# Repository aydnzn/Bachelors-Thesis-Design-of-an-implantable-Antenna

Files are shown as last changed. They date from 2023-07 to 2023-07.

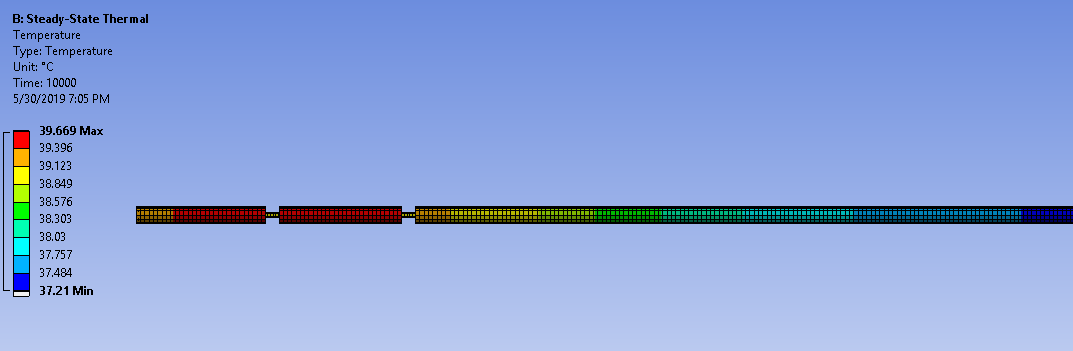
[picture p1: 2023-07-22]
Part I/figs/koichi_in_femur_son.PNG

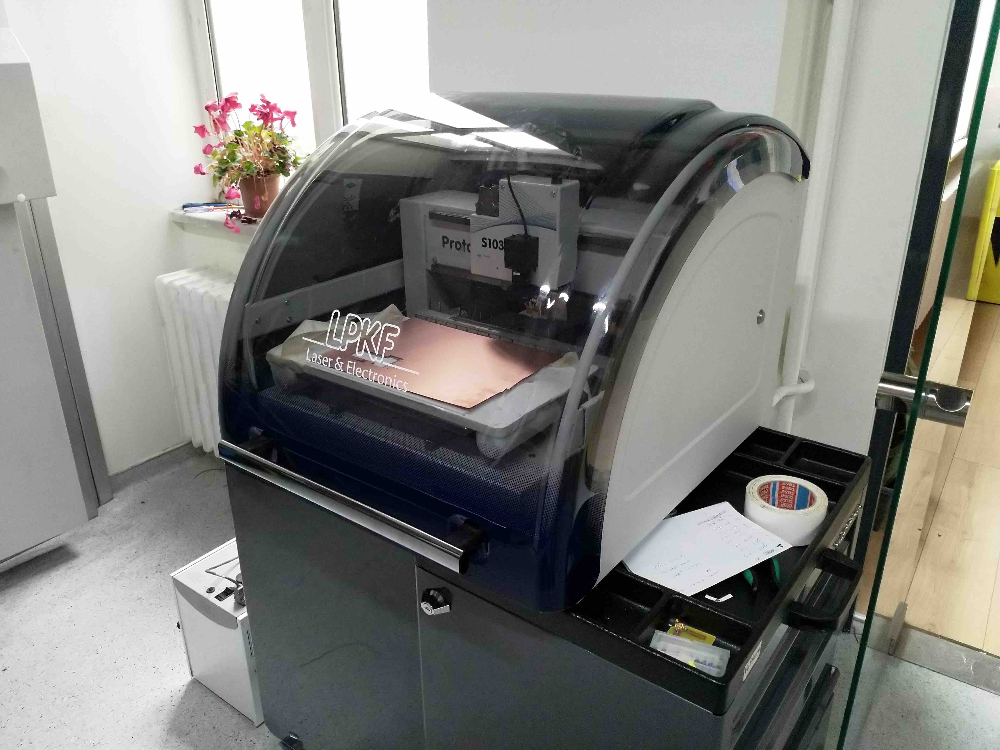
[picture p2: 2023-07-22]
Part II/photos/IMG_20191228_121618.jpeg

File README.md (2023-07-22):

# Bachelor's Thesis: Design of an Implantable Antenna for Microwave Hyperthermia

This Bachelor's thesis, divided into two distinct parts, explores the design of an implantable antenna for microwave hyperthermia. The work was conducted at the Antennas and Propagation Research Laboratory, [BOUNtenna](https://bountenna.boun.edu.tr), at Bogazici University under the guidance of [Assoc. Prof Sema Dumanli Oktar](https://academics.boun.edu.tr/sema.dumanli/).

To access individual parts of the thesis, use the following links: [Part I](./Part%20I/) and [Part II](./Part%20II/).

## Part I

### Project Aim

The primary goal of this project is to utilize technology to augment healthcare services. By designing implantable antennas, we aim to tackle the challenge of post-operative infections, especially those that occur post hip replacement surgeries. The rising trend of such surgeries and the subsequent need for revisions require innovative solutions to mitigate complications like infections. The proposed implants would use microwave hyperthermia to hinder biofilm formation, guided by real-time feedback from the antenna.

### Methodology and Analysis

#### Cavity-Backed Slot Antenna (CBSA)
CBSA was chosen due to its merits like low profile, light weight, and simple integration. Backed by a rectangular cavity for unidirectional radiation, CBSA was designed to operate at 2.4 GHz, a frequency allowed for body area networks or medical applications. The performance of CBSA was measured through return loss and radiation pattern, with the width and length of the stripline identified as crucial parameters post optimization.

#### Coaxial-Slot Antenna
Upon identifying the inadequacy of CBSA in providing adequate heating, a coaxial-slot antenna was modeled. This step validated the effectiveness of the thermal analysis setup, and due to its satisfactory SAR distribution and thermal analysis, the coaxial-slot antenna was chosen as a feasible solution.

#### C-Type Slotted Antenna
A C-type slotted antenna was designed to yield larger SAR values, simulating its performance within a hip implant. Though the heating was improved compared to CBSA, it didn't meet the set criterion for microwave hyperthermia (heating up to 40 °C).

### Conclusion and Future Work

Part I of this project encapsulates the development and simulation of implantable antennas with the aim to combat microwave hyperthermia. Despite facing challenges like defining an exact medium for simulation and limited documentation on Ansys Workbench for biomedical applications, significant knowledge was gained in utilizing HFSS and Workbench software applications.

Future work will focus on designing an antenna with superior heating performance. A wider range of antenna types will be explored and tested with the objective of finalizing a specific design for prototyping. Simulations will be concluded, and the prototyping phase will commence in the subsequent academic semester.

## Part II

This phase began with validating the thermal analysis from Part I, followed by designing a prototype antenna designed for heating at different frequencies. However, limitations led to a shift towards a miniaturized antenna design.

### Methodology

The methodology followed was sequential, starting with prototype antenna design, followed by miniaturized antenna design and measurement setup, phantom development, and concluding with thermal measurements.

A key part of this methodology was identifying the antenna's optimal operating frequency that leads to ideal SAR distribution, a process referred to as heating optimization.

### Prototype Antenna Design
The prototype design was a circular slot antenna, designed to operate at varying frequencies by adjusting the size of the slot. However, limitations arose while testing different frequencies with this setup.

### Miniaturized Antenna Design

Due to limitations faced during the prototype design phase, a transition was made to a more complex miniaturized antenna design, which offered the needed flexibility for testing across different frequencies.

### Measurement Setup

Considerations shifted towards post-production antenna measurements. The material was changed from human bone cortical to human fat for easier phantom production. The antenna was redesigned in the simulation program to fit in the measurement cup, and a feeding structure was added.

### Phantom Development

Phantom development was based on the methodology in this [article](https://ieeexplore.ieee.org/document/7152875), creating an artificial breast phantom replicating the dielectric and thermal properties of human fat. After adjusting the ratios of gelatin, water, and oil, the phantom's dielectric properties proved satisfactory.

### Antenna Production

Antenna production was done using an LPKF device, an in-house printed circuit board prototyping tool. The designed antenna's gerber files were loaded into the LPKF device, after which the feeding structure was soldered onto the antenna.

### Thermal Measurement

Heating at an input power of 6dbm was unobservable due to insufficient measuring equipment. As a result, input power was increased, using a signal generator from another lab. The results obtained were both intriguing and satisfactory.

### Conclusion

Despite several challenges, the project successfully led to the development and simulation of an implantable antenna operating at a frequency of 2.45 GHz. This project provided great learning opportunities and highlighted potential areas for further research and improvements.

### Cost Analysis

The project required a workstation for simulations, a vector network analyzer (VNA), a rotary stage, and absorbers for measurement setup.

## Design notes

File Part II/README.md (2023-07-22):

# Bachelor's Thesis: Design of an Implantable Antenna for Microwave Hyperthermia (Part II)

Welcome to the GitHub repository for the second part of the Bachelor's Thesis. This project focuses on the design of an implantable antenna for microwave hyperthermia. 

This repository contains the second phase of the project, discussing the methodology and analysis undertaken. The initial steps involved verifying the thermal analysis conducted in the previous phase, followed by the design of a prototype antenna for variable frequency heating. Due to encountered limitations, a transition was made to a miniaturized antenna design.

## Methodology

The adopted methodology was a sequential process, starting with the prototype antenna design, followed by the miniaturized antenna design and measurement setup. The subsequent steps involved phantom development and culminated in thermal measurements.

The critical aspect of this methodology was the identification of the optimal operating frequency for the antenna, resulting in ideal SAR distribution - a process also known as heating optimization.

## Prototype Antenna Design

A circular slot antenna served as the prototype design. The design aimed to function at varying frequencies, enabled by changing the size of the slot - the diameter of the inner circle and the width of the slot. Limitations were encountered when testing various frequencies in this setup.

## Miniaturized Antenna Design

The limitations from the prototype antenna prompted a transition to a more intricate miniaturized antenna design. Despite its complexity, this antenna offered the flexibility needed for testing across different frequencies.

## Measurement Setup

The measurement setup phase involved consideration of measurements post-antenna production. The material switched from human bone cortical to human fat for easier phantom production. The antenna was then redesigned in the simulation program to fit into the measurement cup, and a feeding structure was added.

## Phantom Development

Phantom development followed an [article](https://ieeexplore.ieee.org/document/7152875) outlining the creation of an artificial breast phantom replicating the dielectric and thermal properties of human fat. After adjusting the ratios of gelatin, water, and oil, the dielectric properties of the produced phantom proved satisfactory.

## Antenna Production

An LPKF device, an in-house printed circuit board prototyping tool, was used for antenna production. The designed antenna's gerber files were introduced to the LPKF device, after which the feeding structure was soldered onto the antenna.

## Thermal Measurement

At an input power of 6dbm, the heating provided was unobservable due to insufficient measuring equipment. This issue prompted an increase in input power, utilizing a signal generator from another lab. The resultant data were both intriguing and satisfactory.

## Conclusion

Despite a few challenges, a successful development and simulation of an implantable antenna operating at a frequency of 2.45 GHz was accomplished. This project offered invaluable learning opportunities and highlighted areas for potential improvements and further research.

## Cost Analysis

This project necessitated a workstation for simulation implementation and a vector network analyzer (VNA), a rotary stage, and absorbers for the creation of the measurement setup. 

## Repository Structure

This repository holds significant resources and documents pertinent to the project:

- `./scripts` : Contains MATLAB scripts for testing the dielectric properties of the phantom.
- `./designs/` : Holds ANSYS Electronics Desktop (AEDT) files used for various antenna designs throughout the project.
- `./VNA/` : Presents the results from the Vector Network Analyzer.
- `./manufacturing/` : Houses design files used in the fabrication of antennas, boards, etc. 
- `./thermal_photo/` : Features thermal camera screenshots to examine the heat generated by the fabricated antenna.
- `./photos/` : Provides an inside look into the manufacturing and measuring processes through photos.
- `after_graduation.zip` : Contains documents created post-graduation, furthering the work on this project for approximately 3-4 months until the onset of the pandemic.
- `Project_proposal.pdf`: Initial proposal for the project.
- `Midterm_report.pdf`: Midterm report, submitted on 20.11.2019.
- `Presentation.pdf`: Final presentation for this part of the thesis.
- `Bachelor's_Thesis.pdf`: Final bachelor's thesis, submitted on 4th January 2020.
- `./figs/`: Features a collection of screenshots taken during the simulation phase of the research.

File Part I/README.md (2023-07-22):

# Bachelor's Thesis: Design of an Implantable Antenna for Microwave Hyperthermia (Part I)

Welcome to the GitHub repository for the first part of my Bachelor's Thesis on the design of an implantable antenna for microwave hyperthermia. 

## Introduction

This project aims at advancing healthcare by designing an implantable antenna that can combat infections, particularly those that follow hip replacement surgeries. Given the increased trend in hip replacement surgeries and the concomitant need for revisions, a significant focus has been placed on developing solutions to alleviate complications such as infection. These implants are envisioned to use microwave hyperthermia to prevent biofilm formation, facilitated by real-time feedback from the antenna.

## Methodology and Analysis

### Cavity-Backed Slot Antenna (CBSA)
A CBSA, backed with a rectangular cavity for unidirectional radiation, was chosen for its benefits including low profile, light weight, and ease of integration. The CBSA was designed to operate at 2.4 GHz, an allowed band for body area networks or medical applications. The CBSA's performance was assessed in terms of return loss and radiation pattern. After optimization, the most critical parameters identified for matching were the width and the length of the stripline.

### Coaxial-Slot Antenna
After establishing that CBSA cannot provide adequate heating, a coaxial-slot antenna was modeled, which confirmed the success of my thermal analysis setup. The coaxial-slot antenna's SAR distribution and thermal analysis were found satisfactory, hence, it was deemed a viable solution.

### C-Type Slotted Antenna
A C-type slotted antenna was designed to achieve larger SAR values, simulating its performance within a hip implant. Although the heating was improved compared to the CBSA, it did not meet the evaluation criterion for microwave hyperthermia (heating up to 40 °C).

## Conclusion

The project described the development and simulation of implantable antennas aimed at counteracting microwave hyperthermia. Despite challenges such as defining an exact medium for simulation and acquiring limited documentation on using Ansys Workbench for biomedical purposes, substantial learning outcomes were achieved in using the HFSS and Workbench software applications.

## Future Work

The next stages of the project will focus on designing an antenna that demonstrates better heating performance. More antenna types will be reviewed and tested with a goal to finalize a specific antenna for prototyping. Simulations will be completed and the prototyping phase will commence in the next academic semester.

## Repository Structure

This repository contains several important documents and resources related to my project:

- `Project_proposal.pdf`: This document contains the initial proposal for my project.
- `Midterm_report.pdf`: This is my midterm report, which was submitted on 20th March 2019.
- `Presentation.pdf`: Here, you'll find my final presentation for this part of my thesis.
- `Final_report.pdf`: This document is the final report for this part of my thesis, which was submitted on 1st June 2019.
- `./figs/`: This directory contains several screenshots taken during the simulations conducted as part of my research.

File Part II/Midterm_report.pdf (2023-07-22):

EE492

# Senior Design Project Midterm Report

# Design of an implantable antenna for microwave hyperthermia

## Submitted by: Aydın Uzun

## Principal Investigator: Sema Dumanlı Oktar

20.11.2019

### 1. Introduction

The recent technological advancements are revolutionizing the way healthcare is being delivered and they are also a key factor driving the advances of surgical treatment. Joint replacement surgery (hip and knee replacement) is considered the most effective intervention for severe osteoarthritis and hip fractures, reducing pain and disability and restoring some patients to near normal function. [1] As a consequence, hip replacement surgery shows increasing trends in most OECD countries. On average, the rate of hip replacement increased by 30% between 2000 and 2015.[1] Revision burden can be seen as a rough measure of the success of hip replacement surgeries. In the USA the revision burden was 10.2% for hips between 2012 and 2015 [2], but revision surgery of the hip is expensive owing to the increased cost of pre-operative investigations, surgical implants and instrumentation. [3]

The six most common indications for revision after primary hip replacement (listed in order of frequency) are aseptic loosening, pain, adverse soft tissue reaction to particulate debris, dislocation, infection and peri-prosthetic fracture.[4] Especially performing the revision surgery for infection is riskier considering the instrumentation. Staphylococcus aureus and Staphylococcus epidermidis are the leading etiologic agents of orthopedic implant infection.[5] Traditional antibiotic therapy will never be successful against these pathogens after the biofilm is formed. [6] This property of bacteria is called antimicrobial resistance (AMR) and it is a major concern worldwide. The other modes of treatment will be needed to prevent biofilm formation in the first place.

A hip implant can be equipped with sensors and microelectronics forming a wireless communication link between the implant and an on-body sensor to collect continuous data or provide real-time feedback.[7] In this project it is aimed to design an antenna taking action against infection before and during the biofilm formation through microwave hyperthermia with the help of the feedback from the antenna which monitors its environment.

### 2. Objectives

The objective of this project is to take action against infection through microwave hyperthermia. In this context, the electrical characteristics of the tissue surrounding the implant will be determined immediately after the operation. (when the infection is present) In addition to that, numerical and physical modelling of the propagation environment will be performed. After all of the optimizations are completed, the optimum working frequency for the microwave hyperthermia will be determined and the antenna design will be completed.

The second objective of this project is to develop the phantom and to build the measurement setup on which the measurements will be performed next semester.

### 3. Approach and Methodology

a. Optimizations for microwave hyperthermia

Because the human body absorbs electromagnetic waves it is often difficult to connect an implanted device to the outside world. The effect of hyperthermia depends on the depth of the implant, surrounding tissues and near field losses. It should be noted that the surrounding tissue properties and depth of the implant vary from patient to patient, but only in one patient as the patient ages. Therefore, an antenna which can adapt to the changing environment and target energy to the required region should be designed for microwave hyperthermia. The antenna parameters will be optimized considering both the thermal and electromagnetic distribution.
b. Phantom development and building of measurement setup

1- Digital 3D design of the phantom model

A 3D model will be developed to mimic the environment in which the hip implant will be located in real life. The model should include the hip implant, a portion of the femur, pelvis, body fluid, hip muscle, fat and skin.
2- The integration of 3D phantom model with liquid/gel phantoms

The printed 3D model should be filled up with liquid/gel in accordance with the approximate dielectric constant and conductivity values of the corresponding parts described above.
3- Development of measurement setup

A test kit will be developed for measuring the input response and the transmission response of the designed antenna. The test kit will consist of a mini vector network analyzer (VNA), a rotary stage and absorber material. The test kit will be used in system level tests too.

### 4. Work Completed

In the first part of the project (EE 491), great progress had been made. You can review my previous reports to see what I did. At the beginning of the semester a meeting was held with my supervisor and we talked about what we are going to do this semester.

It was important to test that we did the thermal analysis correctly. The coaxial-slot antenna of Koichi Ito is designed and tested accordingly. The further explanation can be found on the final report of first part of the project.

The first task of this semester was to design a prototype antenna to test heating at different frequencies. One can see the prototype antenna and measurement setup on Figure
1. It is a circular slot antenna. To operate this antenna at the different frequencies (0.5 GHz to 2.5 GHz) one should definitely change the size of the slot in other words change the diameter of the inner circle and the width of the slot. One can also the change of the slots of antennas operating at 2 GHz and 2.5GHz on Figure 2 and Table 1.

This first task was very critical, because doing this we can find the optimum operating frequency value of the antenna which results in perfect SAR distribution. This process is also called heating optimization. It is clear that the heating occurs because of near field losses and it is frequency dependent. We have the possibility to test different frequencies unlike the Koichi’s circular slot antenna, because for our purposes only the specific small neighborhood of the antenna is important, not the depth or area of the heated region.

To determine the antenna’s working frequency is also important because I should also get a transmitter which works at this frequency value. So, it is an initial step for prototyping.

This was a simple setup as one can also see on Figure 1, but things did not go the way we wanted. We concluded that testing different frequencies is difficult in this setup. The limitation was that I could not change the antenna size as much as I wanted. To overcome this obstacle, it was decided to use a miniaturized antenna. The setup can be seen on Figure3. This design is initially made by my supervisor Prof. Sema Dumanlı Oktar. It is a complex design and was a little bit hard to understand. But after spending some time on the model I got it.

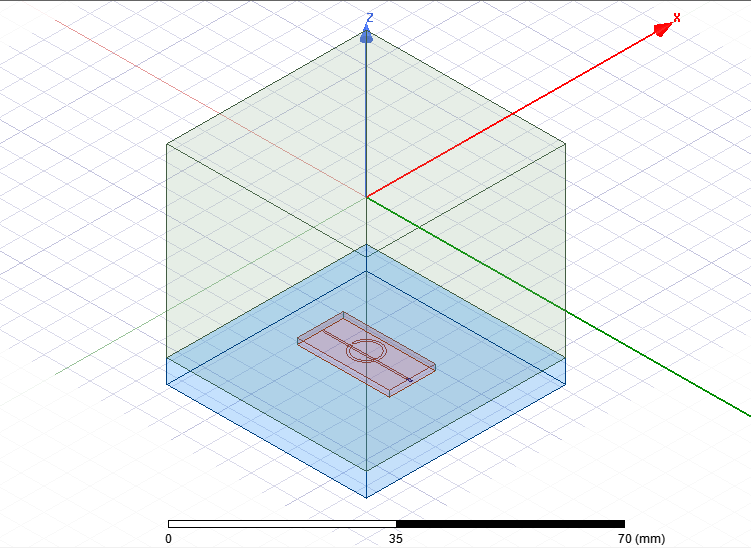
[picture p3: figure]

Figure 1: Measurement setup

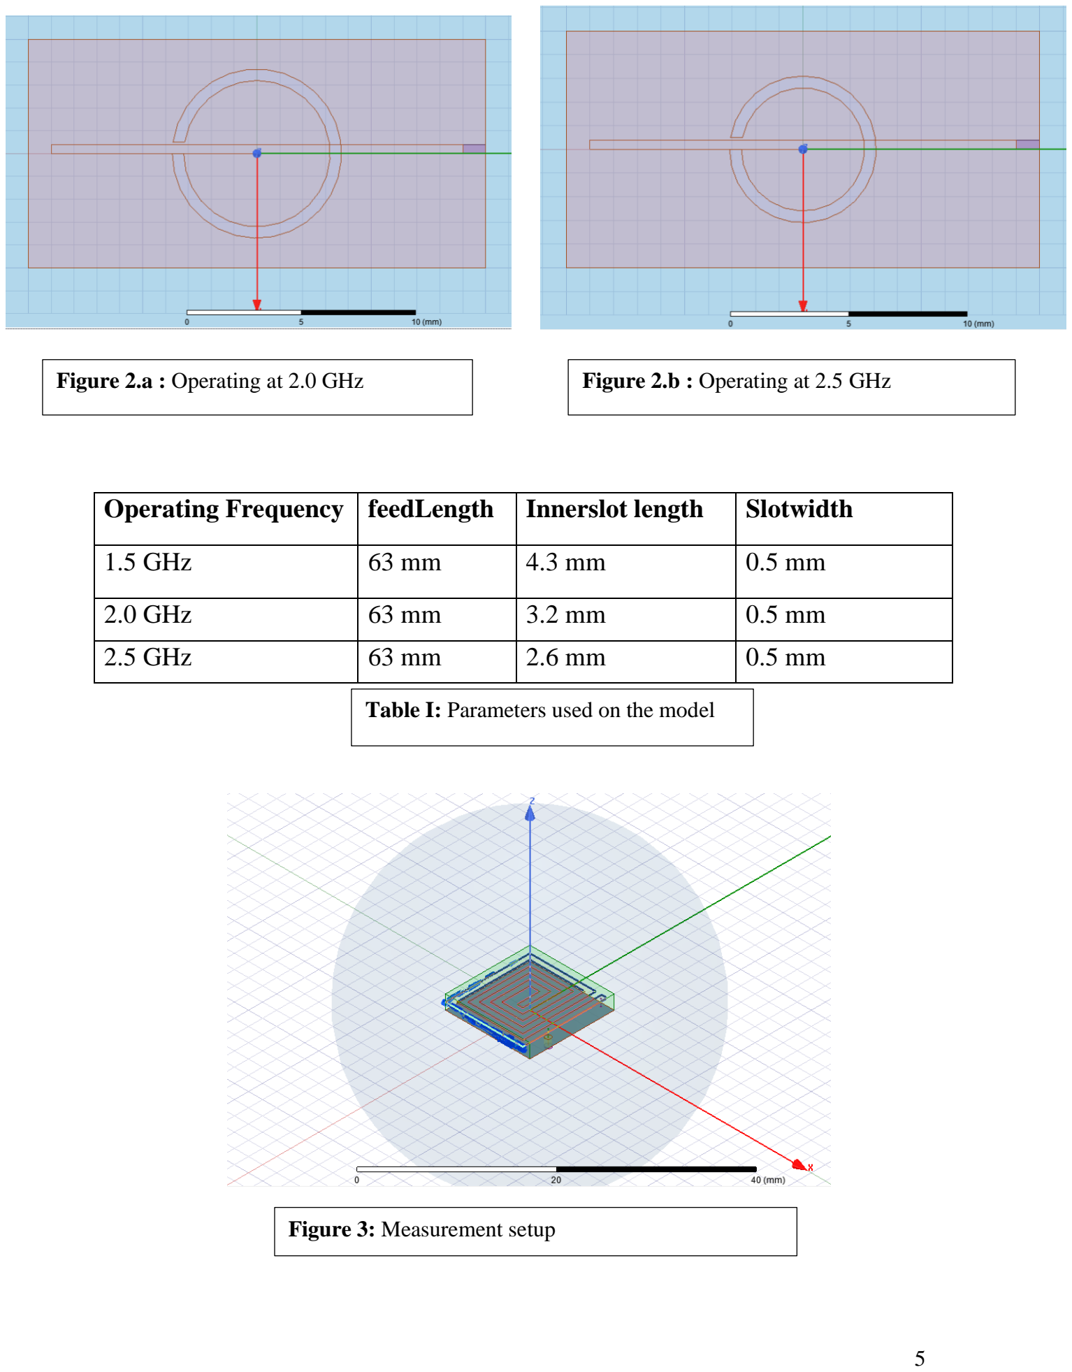
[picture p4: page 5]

Operating Frequency | feedLength | Innerslot length | Slotwidth
1.5 GHz | 63 mm | 4.3 mm | 0.5 mm
2.0 GHz | 63 mm | 3.2 mm | 0.5 mm
2.5 GHz | 63 mm | 2.6 mm | 0.5 mm
Figure 2.a : Operating at 2.0 GHz | Figure 2.b : Operating at 2.5 GHz

Table I: Parameters used on the model

Figure 3: Measurement setup

The antenna is inside a spherical medium which is human bone cortical. The antenna consists of a labyrinth like slot, a ground plane, implant substrate and feeding mechanism. An optimization process has done like before. Only by changing the slot width of the labyrinth like slot the antenna is matched at different frequencies. You can see the related S-parameters plot below.

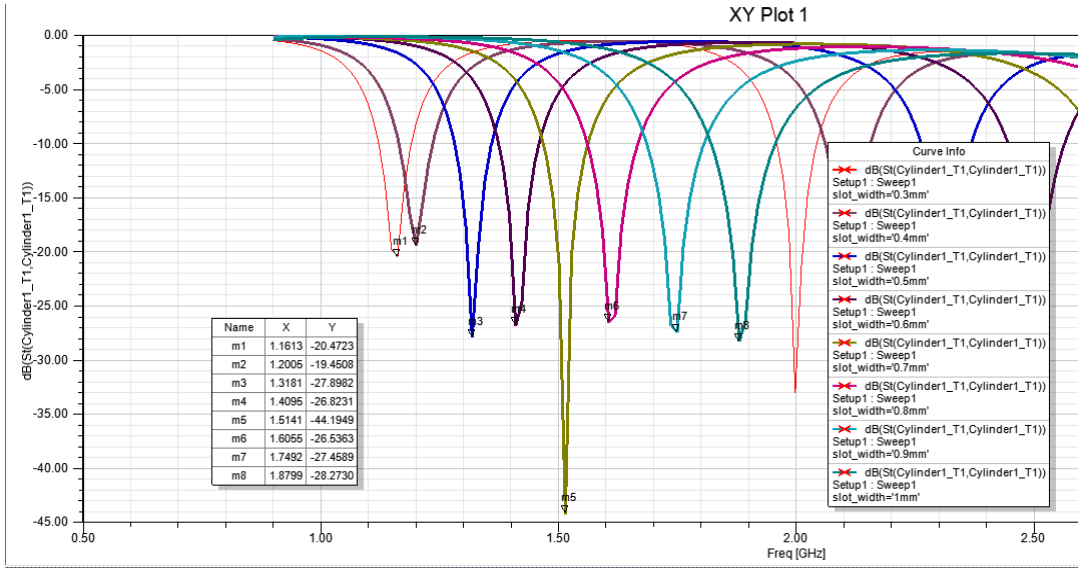
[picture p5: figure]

One can see here the antenna has perfectly matched to operate at different frequencies. After deciding the slot widths of the labyrinth like antennas and their corresponding frequencies (see Table II). Specific simulations at specific frequencies were performed and electric fields were calculated accordingly. The SAR plots were drawn and interpreted with my advisor. You can see the SAR plots seen from different angles below. (Figure 5 to Figure 12)

Figure 4: S parameters plot

Working frequency | Slot width
1.16 GHz | 0.3 mm
1.20 GHz | 0.4 mm
1.31 GHz | 0.5 mm
1.41 GHz | 0.6 mm
1.51 GHz | 0.7 mm
1.60 GHz | 0.8 mm
1.75 GHz | 0.9 mm
1.88 GHz | 1.0 mm

Table I: Slot widths and corresponding working frequencies

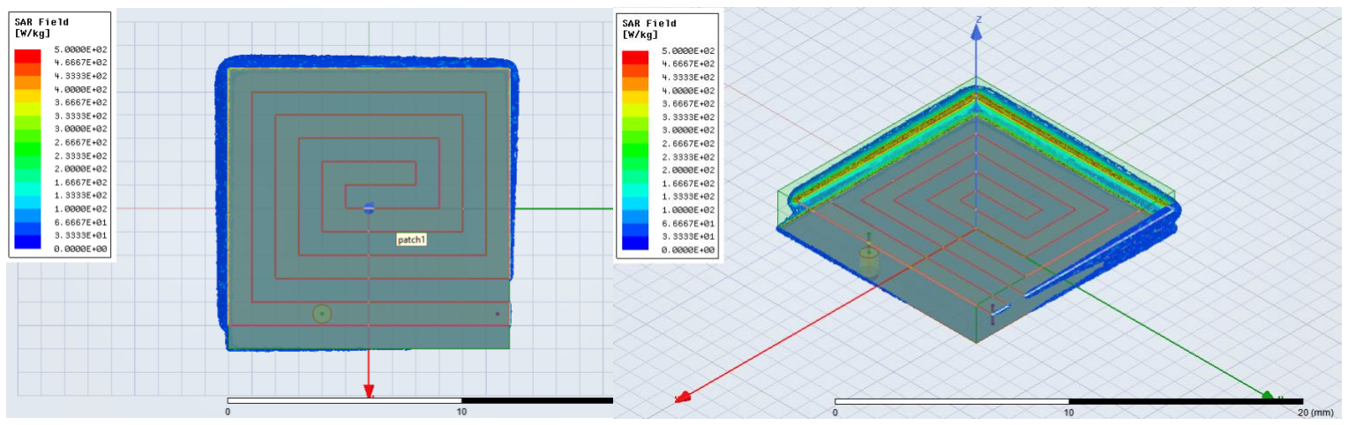
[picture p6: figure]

Figure 5: SAR distributions at 1.88 GHz seen from different angles

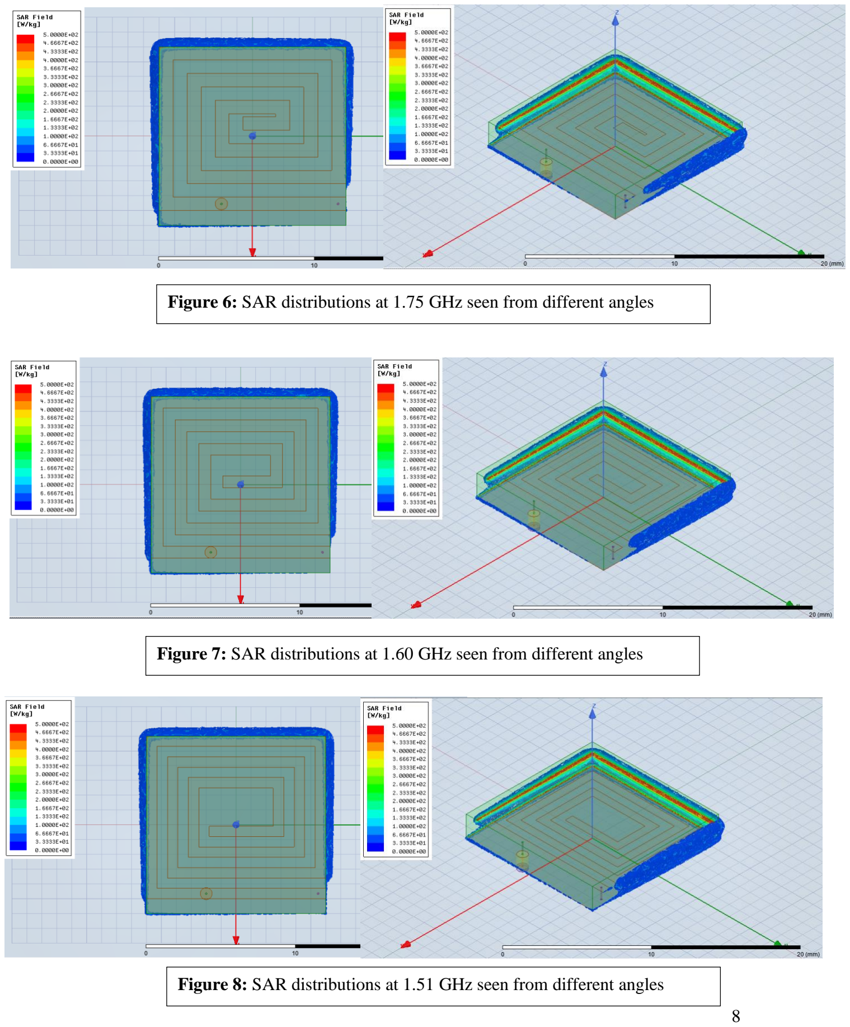
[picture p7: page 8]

Figure 6: SAR distributions at 1.75 GHz seen from different angles

Figure 7: SAR distributions at 1.60 GHz seen from different angles

Figure 8: SAR distributions at 1.51 GHz seen from different angles

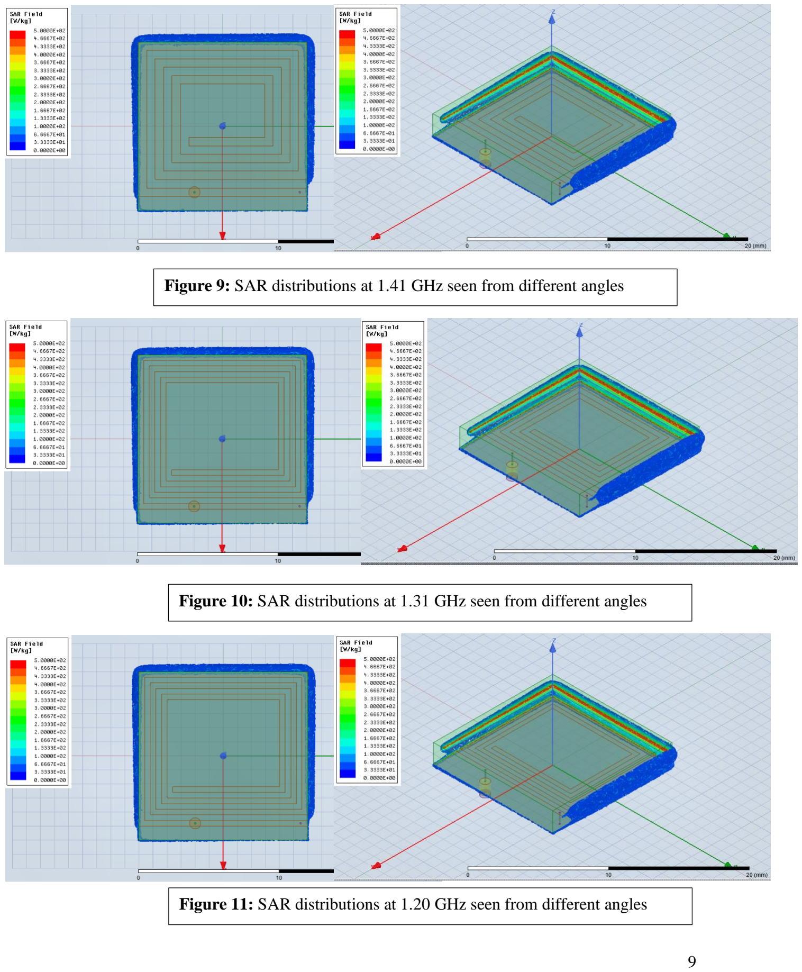
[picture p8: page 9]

Figure 9: SAR distributions at 1.41 GHz seen from different angles

Figure 10: SAR distributions at 1.31 GHz seen from different angles

Figure 11: SAR distributions at 1.20 GHz seen from different angles

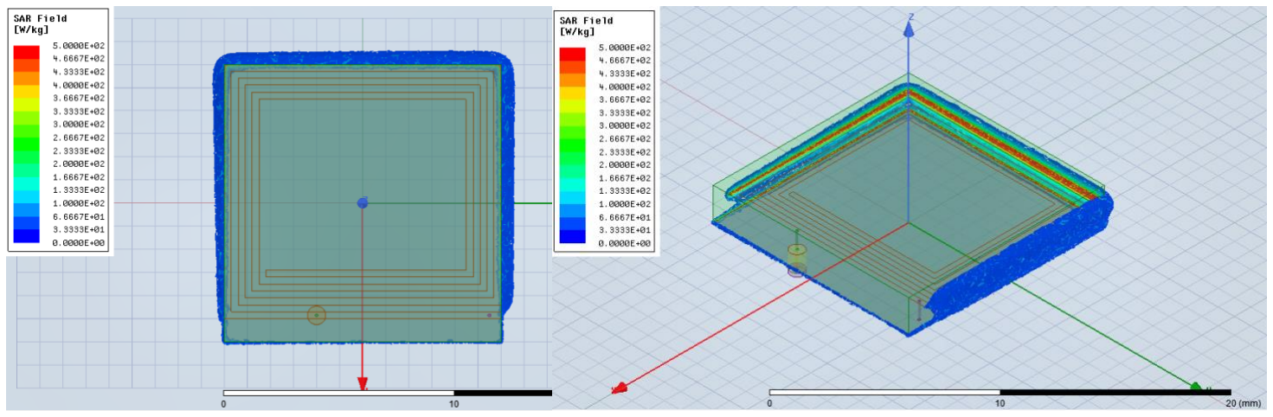
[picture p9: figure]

According to these results, one can obtain a better SAR distribution at lower frequencies.

### 5. Work to Be Completed

Literature review | EE 491
Power-density-based optimization | Single Layer

Cylindrical Layer

Detailed Layer

Temperature-based
optimization

Single Layer

Cylindrical Layer

Detailed Layer

Report & Presentation

Working frequency optimization on two different models | 02.10.2019 – 20.11.2019
Last simulations | 20.11.2019 – 30.11.2019
Prototyping | Antenna element | 01.12.2019 – 12.12.2019
Measurements | System level measurements | 12.12.2019 – 19.12.2019

Heating measurements

Report & Presentation | 20.12.2019 – 31.12.2019

The antenna parameters will be optimized using outputs of each layer structure as feedbacks step by step from the simplest one (single layer) to the most complicated one (detailed layer) considering both power density-based optimization and temperature-based optimization and hence, they will be considered as a whole.

### 6. Realistic Constraints

Figure 12: SAR distributions at 1.16 GHz seen from different angles a. Social, Environmental and Economic Impact

Although from an economical point of view, the project does not aim for any profit or further labor, if the project will turn out to be a real success, then it will yield a great economic and social benefits for users and device manufacturers. Moreover, using the designed antenna will save the patients and physicians a lot of time, because the implant antenna has its own feedback mechanism. Implicitly it will reduce the cost associated with the healthcare and it will improve the healthcare provided. It is a fact that implanted wireless devices are going to find wider application in tomorrow’s world. Whether my project will be completed successfully is not going to change this fact.
b. Cost Analysis

The project requires a workstation on which the simulations to be implemented. I will be using the workstation of BOUNTENNA during my project. To create the measurement setup a vector network analyzer (VNA), a rotary stage and absorbers will be used. In addition to these costs, a 3D printer and chemicals will be used to create the phantom which should imitate the biological tissue. These materials should also be included in the costs. Moreover, I will be investing a specified amount of time for this project throughout the year. My plan is to work at least for three days each week for a faster progress.

c. Standards

In this project, the engineering ethics and code of conduct will be considered. Besides, the IEEE, IET, ETSI and EU standards will be followed in addition to Turkish standards.

### 7. References

[1] OECD (2017), “Hip and knee replacement”, in Health at a Glance 2017: OECD Indicators, OECD Publishing, Paris.
[2] Third AJRR Annual Report on Hip and Knee Arthroplasty Data. (2016). [ebook] Rosemont, Illinois: American Joint Replacement Registry, pp.13-21. Available at: http://www.ajrr.net/images/annual_reports/AJRR_2016_Annual_Report_final.pdf [Accessed 21 Feb. 2019].
[3] Vanhegan, I. S., Malik, A. K., Jayakumar, P., Islam, S., Haddad, F. S. 2012. “A financial analysis of revision hip arthroplasty: the economic burden in relation to the national tariff”, J Bone Joint Surg Br, 94(5), 619-623.
[4] The NJR Editorial Board, Ed., “National Joint Registry 13th Annual Report 2016,” rep., 2016.
[5] L. Montanaro, P. Speziale, D. Campoccia, S. Ravaioli, I. Cangini, G. Pietrocola, S. Giannini, and C. R. Arciola, “Scenery of Staphylococcus implant infections in orthopedics,” Nov-2011. [Online]. Available: https://www.futuremedicine.com/doi/pdf/10.2217/fmb.11.117. [Accessed: 20-Feb-2019].
[6] G. D. Ehrlich, F. Z. Hu, Q. Lin, J. W. Costerton, and J. C. Post, “Intelligent implants to battle biofilms | Request PDF,” 03-Nov-2004. [Online]. Available:
https://www.researchgate.net/publication/292688877_Intelligent_implants_to_battle_biofilms. [Accessed: 20-Feb-2019].
[7] | S. Dumanli, “A cornered shallow cavity backed slot antenna suitable for smart hip implants,” | 2016
| 10th European Conference on Antennas and Propagation (EuCAP), 2016.

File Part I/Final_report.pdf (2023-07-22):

DESIGN OF AN IMPLANTABLE ANTENNA FOR MICROWAVE HYPERTHERMIA

by

Aydın Uzun

A report submitted for EE491 senior design project class in partial fulfillment of the requirements for the degree of Bachelor of Science
(Department of Electrical and Electronics Engineering) in Boğaziçi University

June 1st, 2019

Principal Investigator: Sema Dumanlı Oktar

i

ACKNOWLEDGMENTS

I would like to thank Prof. Sema Dumanlı Oktar for her understanding; and for giving

me the opportunity to work on her project SlmpliFy-B (Smart Orthopaedic Hip

Implant Fighting Antimicrobial Resistant Bacteria.

ii

ABSTRACT

Technology today affects every single aspect of modern society. In fact, there is not an industry

out there that has not been affected by the hi-tech revolution. Whether we are talking about

transportation, communication, security, banking or healthcare, they all rely on technology in

one way or another. But nowhere is this immense impact more apparent than in the field of

medicine and healthcare. Technological advancements are revolutionizing the way healthcare

is being delivered and are also a key factor driving the advances of surgical treatment. But we

are still far from fighting against orthopedic implant infection without major intervention and

revision surgery. Staphylococcus aureus and Staphylococcus epidermidis are the leading

etiologic agents of orthopedic implant infection. Traditional antibiotic therapy will never be

successful against these pathogens after the biofilm is formed. This property of bacteria is called

antimicrobial resistance (AMR) and it is a major concern worldwide.

A hip implant can be equipped with sensors and microelectronics forming a wireless

communication link between the implant and an on-body sensor. In this project an antenna

taking action against implant infection before and during the biofilm formation through

microwave hyperthermia will be designed.

iii

TABLE OF CONTENTS

CHAPTER

iv

LIST OF FIGURES

Figure 1: Modelled CBSA | 3-4

v

LIST OF TABLES

1 | 7

CHAPTER 1

INTRODUCTION

The recent technological advancements are revolutionizing the way healthcare is being

delivered and they are also a key factor driving the advances of surgical treatment. Joint

replacement surgery (hip and knee replacement) is considered the most effective intervention

for severe osteoarthritis and hip fractures, reducing pain and disability and restoring some

patients to near normal function. [1] As a consequence, hip replacement surgery shows

increasing trends in most OECD countries. On average, the rate of hip replacement increased

by 30% between 2000 and 2015.[1] Revision burden can be seen as a rough measure of the

success of hip replacement surgeries. In the USA the revision burden was 10.2% for hips

between 2012 and 2015 [2], but revision surgery of the hip is expensive owing to the increased

cost of pre-operative investigations, surgical implants and instrumentation. [3]

The six most common indications for revision after primary hip replacement (listed in order of

frequency) are aseptic loosening, pain, adverse soft tissue reaction to particulate debris,

dislocation, infection and peri-prosthetic fracture.[4] Especially performing the revision

surgery for infection is riskier considering the instrumentation. Staphylococcus aureus and

Staphylococcus epidermidis are the leading etiologic agents of orthopedic implant infection.[5]

Traditional antibiotic therapy will never be successful against these pathogens after the biofilm

is formed. [6] This property of bacteria is called antimicrobial resistance (AMR) and it is a

major concern worldwide. The other modes of treatment will be needed to prevent biofilm

formation in the first place.

A hip implant can be equipped with sensors and microelectronics forming a wireless

communication link between the implant and an on-body sensor to collect continuous data or

provide real-time feedback.[7] In this project it is aimed to design an antenna taking action

against infection before and during the biofilm formation through microwave hyperthermia

with the help of the feedback from the antenna which monitors its environment.

CHAPTER 2

METHODOLOGY AND ANALYSIS

### 2.1 Design of CBSA

After literature review it is decided to use a cavity-backed slot antenna, because the cavity

backed slot antenna (CBSA), where the slot is backed with rectangular cavity, achieves

unidirectional radiation and has advantages of low profile, light weight and ease of integration.

[8] The CBSA can be fed by probe, metal waveguide, substrate integrated waveguide (SIW),

and microstrip, but the microstrip-fed CBSA has simple structure and small size. [8]

2.1.a In vacuum

In this step a CBSA is designed to operate at 2.4 GHz. The industrial, scientific and medical

(ISM) 2.40 GHz radio band is an allowed band for body area networks or medical applications.

[9] The performance of designed antenna is judged by its return loss and radiation pattern.

z

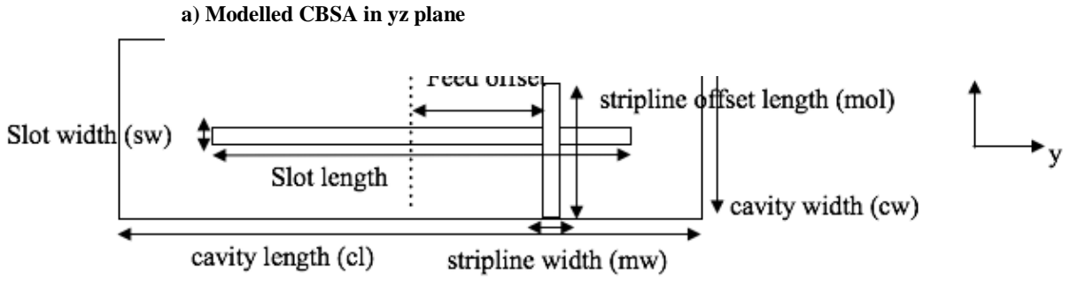
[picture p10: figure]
a) Modelled CBSA in yz plane

b) Modelled CBSA in xy plane

The model of the designed antenna can be seen in Figure 1 from different perspectives. The

dimensions of the model can be found in Table I.

The cavity is formed from a 3.15 mm thick (cavity height) substrate with a dielectric constant

of 4.4 (FR-4). The slot is fed by a 50Ω stripline located in the vertical midplane of the antenna

in z direction.

The initial dimensions other than the cavity height are determined using the HFSS Antenna

Toolkit Software. Prior to the start of the optimization, the software introduces a microstrip

feed slot antenna with the initial values of Table I, but this is not the desired antenna. After

some modifications, the desired antenna is achieved, the model of which is shown in Figure 1.

The CBSA has been optimized for operation at 2.4 GHz with -20dB return loss. The

optimization is done using software ANSYS Electromagnetics Suite. The dimensions given in

Table I are parametrized and optimized for a return loss -20dB.

One conclusion that can be drawn from the optimization process is that the most critical

parameters for matching are the parameters for the width of the stripline and the length of the

stripline. In addition, sloth length is the most critical parameter in terms of CBSA resonance

frequency.

The return loss curve of the optimized antenna can be seen in Figure 2.

Figure 1: Modelled CBSA

c) Modelled CBSA in xz plane

2.1.a In fat

The same procedure is used as in vacuum. The initial values of parametrized dimensions of the

antenna optimized in fat are the final values of the antenna optimized in vacuum. It is obvious

that the dimensions should change significantly to cause a return loss of -20dB, since

Dimension | Initial value | Final value
Slot length | 5.56 cm | 5.2 cm
Slot width | 0.28 cm | 0.21 cm
Feed Offset | 1.55 cm | 1.8 cm
Stripline width | 0.31 cm | 0.15 cm
Stripline offset length | 1.71 cm | 0.53 cm
Cavity length | 11.1 cm | 8.1 cm
Cavity width | 8.3 cm | 3.2 cm

Table I. Parametrized dimensions of CBSA in vacuum

Figure 2: Simulated S11 vs Frequency

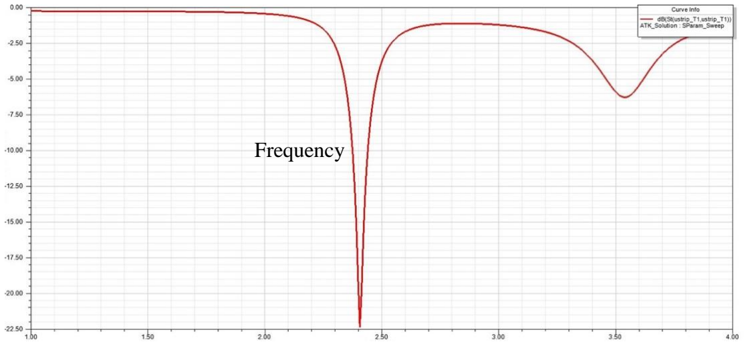
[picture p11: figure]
Frequency

|S11| (dB)

the electrical properties of vacuum and fat are completely different. The dimensions of the

model shown in Figure 1 are shown in Table II. The return loss curve of the optimized antenna

can be seen in Figure 3.

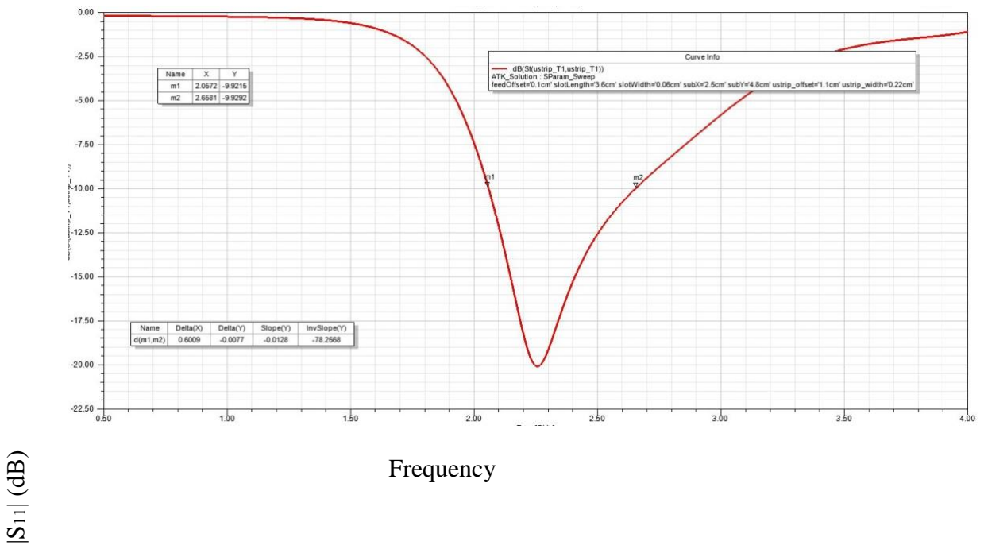
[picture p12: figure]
Figure 3: Simulated S11 vs Frequency; Frequency

2.1.c Thermal Analysis

The model is already set up in HFSS to prepare it for thermal analysis. The HFSS geometry

and the associated solution data should be transferred to ANSYS Workbench and the thermal

analysis carried out in ANSYS Workbench. The thermal properties of the materials should be

Dimension | Initial value | Final value
Slot length | 5.2 cm | 3.6 cm
Slot width | 0.21 cm | 0.06 cm
Feed Offset | 1.8 cm | 0.1 cm
Stripline width | 0.15 cm | 0.22 cm
Stripline offset length | 0.53 cm | 1.1 cm
Cavity length | 8.1 cm | 4.8 cm
Cavity width | 3.2 cm | 2.5 cm

Table II. Parametrized dimensions of CBSA in fat introduced to the software. [10] Thereafter, heat dissipation should be specified by assigning

convection to the exterior surfaces of the structure. In addition, it should be introduced into

software which objects introduce heat effect to calculate the thermal properties. There are two

types of imported loads: heat flux, heat generation. The designed model should have both,

because there exist volume losses caused by currents flowing in the volumes of lossy dielectrics

and surface losses caused by currents flowing in the volumes of lossy dielectrics. After

completing these steps, the temperature of the entire model can be displayed. However, the

thermal demonstration of CBSA was not satisfactory. | The temperature increases from 37 | °C
to 37.13 | °C.

In the antennas for telecommunications and broadcasting, input impedance, radiation pattern

and radiation efficiency are among the important factors for performance evaluation. In

contrast, in antennas for thermal treatment, it is the specific absorption rate (SAR) and the

temperature distribution in the body that are the important criteria.[11]
Figure 4: Simulated SAR distribution of CBSA

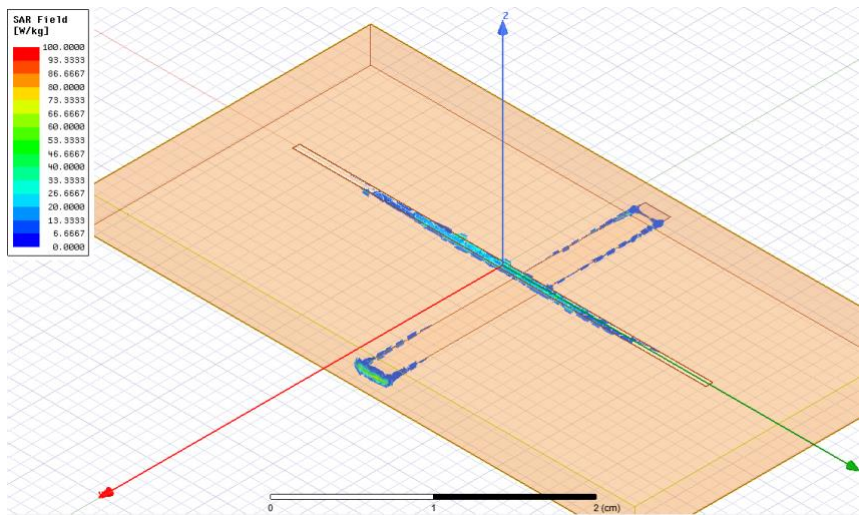
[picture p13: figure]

Figure 4 shows the simulated SAR distribution around the CBSA. Here the CBSA is inserted

into human fat tissue ( εr = 5.28, σ = 0.102 S/m at 2.4 GHz) [12]. The relative high SAR region

exists only around the slot and the tip of the microstrip. But the region is so small that a

prototyped antenna is going to definitely fail the heating of the surrounding tissue.

Having understood the fact that a CBSA cannot provide a good heating, a literature review has

done to understand which type of antennas have been developed and reported in the literature.

After literature review, it is decided to model the coaxial-slot antenna. [13]

### 2.2 Modelling of Coaxial-Slot Antenna

The coaxial-slot antenna is composed of a thin semi-rigid coaxial cable. Some ring slots are cut

on the outer conductor of the thin coaxial cable and the tip of the cable is short circuited. The

operating frequency is 2.45 GHz, which is one of the Industrial, Scientific, and Medical (ISM)

frequencies. Figure 5 and Table 3 show the basic structure and the structural parameters of the

antenna. The performance of modelled antenna is judged by its thermal analysis and SAR

distribution.

Figure 5: Basic structure of the coaxial-slot antenna [14]

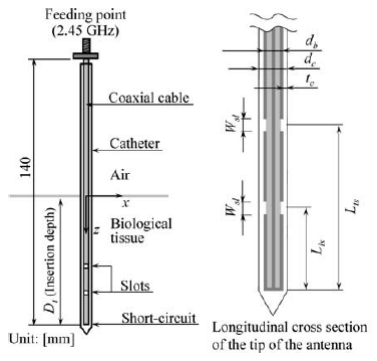
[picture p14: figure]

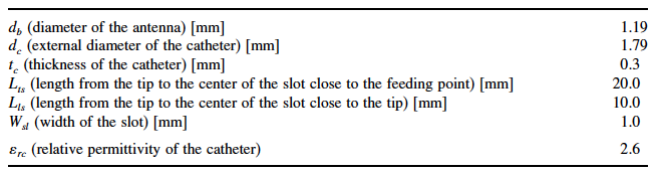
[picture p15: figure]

Modelling of this antenna gives the opportunity to check my thermal analysis setup. The

coaxial-slot antenna was already modelled and analyzed electrically and mechanically.

Comparing my simulated results and given results in the paper. [16] I concluded that my

thermal analysis setup mentioned in previous section of this chapter is successful. Figure 6

shows the geometry of modelled antenna in HFSS and figure 7 shows its simulated SAR. The

observation planes are x-z and x-y planes. The high SAR region exists only around the tip of

the antenna. One can compare the simulated and measured SAR region in figure 8, they are

similar as expected.

Table III. Structural parameters of the coaxial-slot antenna with two slots [15]

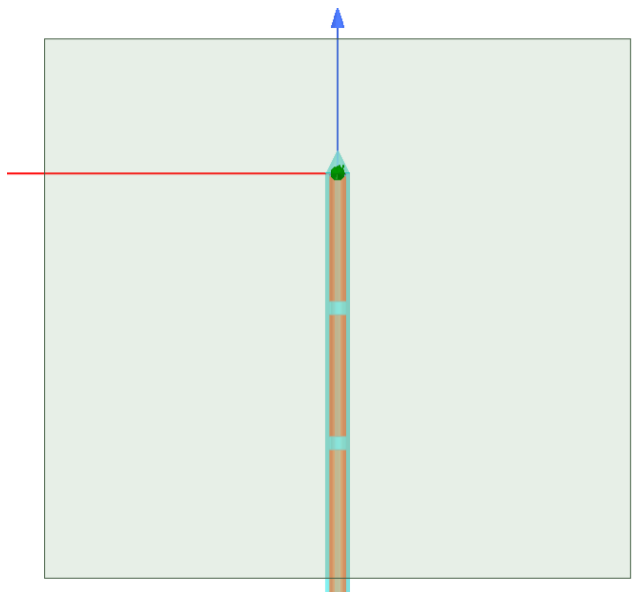
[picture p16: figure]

Figure 6: Modelled coaxial-slot antenna

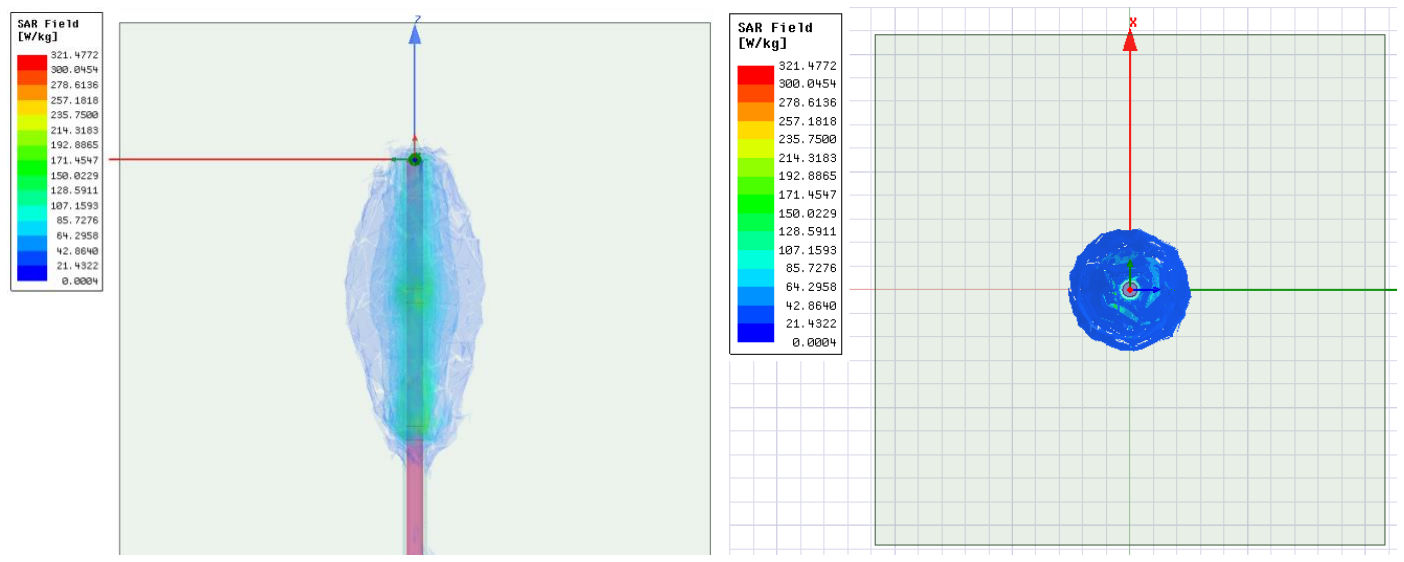
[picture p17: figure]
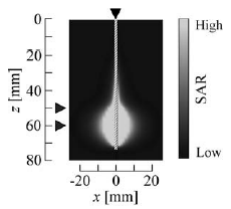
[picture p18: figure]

After observing the SAR values of modelled antenna are satisfactory, the thermal

analysis of the modelled antenna should be done. The HFSS geometry and the associated

solution data is transferred to ANSYS workbench and the thermal analysis carried out in

ANSYS Workbench. For the simulations the net input power of the antenna is 5.0 W. The

heating time is 600s. In addition, the initial temperature of the biological tissue (muscle) is 37

ºC. The surrounding tissue’s electrical and thermal properties are : εr (relative permittivity)=

47 , σ (conductivity in S/m ), = 2.21, c (specific heat in J/ Kg.K) = 3500, κ(thermal conductivity

in W/m.K) = 0.60, ρ( density in kg/m³
) = 1020. [18] The figure 9 shows the simulated

temperature distribution and the figure 10 shows the measured temperature distribution. They

are also similar as expected.

Figure 7: Simulated SAR distribution of the modelled antenna

Figure 8: Measured SAR distribution [17]

b) xz plane | a) xy plane

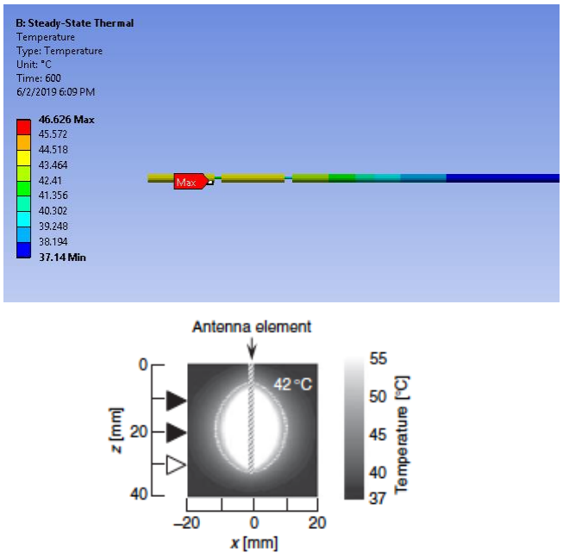
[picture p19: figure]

After observing that my simulation works with no problem, I started to think about the question

what type of antenna I can use in my project for a better heating simulation in other terms for

an antenna with large SAR values. After meetings with my principal investigator and some

literature review, I decided to use C type slotted antenna.

### 2.3 Design of an antenna with C type slots

The designs of C type slotted antenna and coaxial-slot antenna are similar. This is why

one should expect large SAR values in the neighborhood of the antenna. In figure 11 one can

see the basic structure of the designed antenna. The substrate used in this antenna design is

Rogers RO3210 which has the electrical property εr = 10.2. The surrounding tissue is cortical

Figure 9: Simulated temperature distribution

Figure 10: Measured temperature distribution bone (εr = 1.14, σ =0.385 S/m). [19] The parameters of the designed antenna can be seen on the

table IV.

This antenna is simulated inside the hip implant designed by Sema Dumanlı Oktar. On

figure 12 one can see the combination of the hip implant and designed antenna. On figure 13

one can see the simulated SAR distribution of the designed antenna. The observation planes are

xy and xz planes. The high SAR region exists around the slots of the antenna and the regions

are far wider than the SAR regions of my first antenna (cavity backed slot antenna).

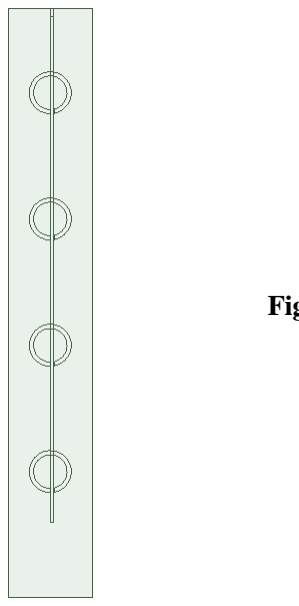
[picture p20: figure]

Size of antenna | 10 mm x 70 mm
Thickness of substrate | 1.28 mm
Feed length | 60 mm
Inner radius of C type slot | 2 mm
Outer radius of C type slot | 2.5 mm

Figure 11: Basic structure of the designed antenna

Table IV. Parameters of the antenna with C type slots

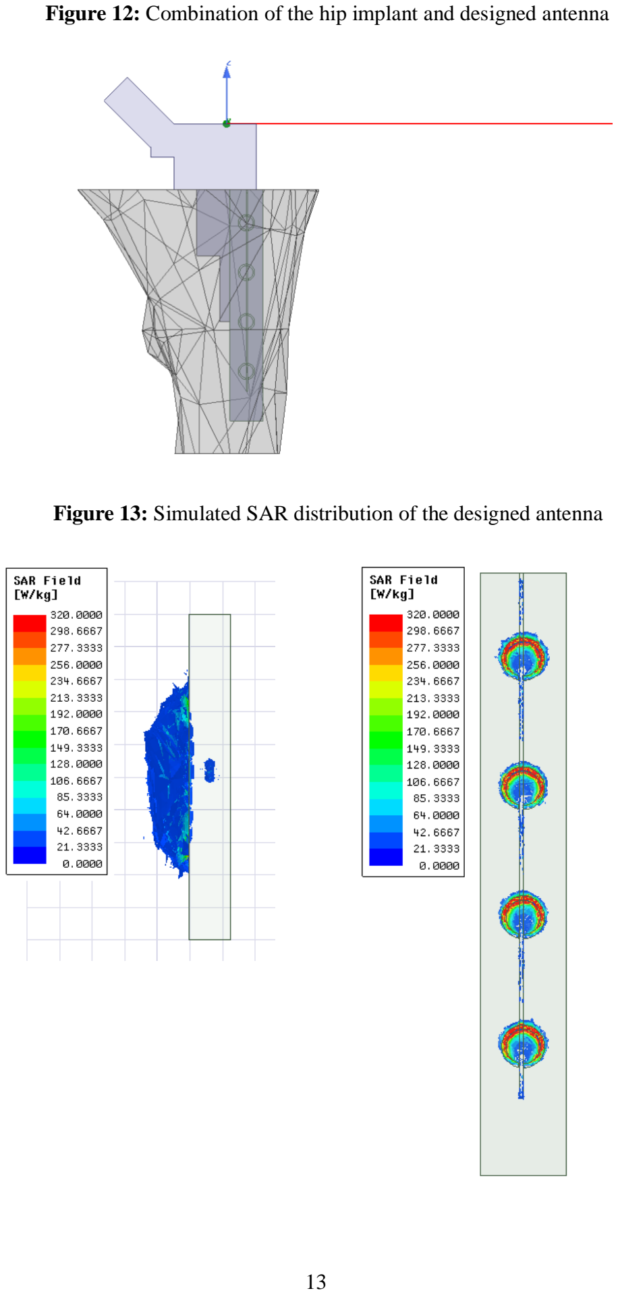
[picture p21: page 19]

Figure 12: Combination of the hip implant and designed antenna

Figure 13: Simulated SAR distribution of the designed antenna

The HFSS geometry and the associated solution data is transferred to ANSYS

Workbench and the thermal analysis carried out in ANSYS Workbench. The thermal properties

of the materials are also introduced to the software. After completing necessary steps mentioned

before, the temperature of the entire model can be displayed. The temperature around the slots

increases from 37 | °C to 38.53 | °C. Even though the result is much better than the result of my

first designed antenna, it does not meet the aforementioned evaluation criterion for the

microwave hyperthermia, whether the 1 mm neighborhood of the designed antenna can be

heated up to 40 °C.

CHAPTER 3

CONCLUSION

### 3.1 Results and Discussion

In this project the development and simulation of an implantable antenna taking

action against microwave hyperthermia operating at the frequency of 2.45 GHz have

been described. The project started with a simple antenna design. Thanks to this simple

antenna design, I learned to use the HFSS software. Some parametric analysis was done

and the effect of changes of these parameters on the resonant frequency of the cavity

backed slot antenna was observed. For example, doing this I made the conclusion that

slot length is the most critical parameter for determining the resonant frequency of

cavity backed slot antenna. Afterwards, the same analysis is done to the cavity backed

slot antenna in human fat tissue. The effect of medium on the antenna characteristics is

observed. Changing antenna parameters, the return loss of -20 dB is achieved. The

bandwidth of the antenna is also increased.

After electromagnetics analysis the thermal analysis is done, and I learned to use

software ANSYS Workbench during my project. But the thermal demonstration of

cavity backed slot antenna was not satisfactory, only an increase of 0.13 °C is observed.

The main reason for this was the distribution of the SAR. The region was so small.

Although the result of cavity backed slot antenna was not satisfactory, the design and

simulation of cavity backed slot antenna electrically and mechanically helped me a lot

practicing the applications HFSS and Workbench.

It would be nice to have a reference for my thermal analysis. Because I am not sure if

my thermal analysis setup is successful or not. I may have made a mistake when

applying heat transfer between surfaces. To clarify this question, it would be good to

model an antenna, which has developed and reported in literature. For this purpose, I

modeled the coaxial-slot antenna, developed by Koichi Ito and Kazuyuki Saito.

The performance of the coaxial-slot antenna is not judged by its return loss and

radiation pattern, but by its specific absorption rate (SAR) and the temperature

distribution. It is observed that the SAR values of the modelled antenna satisfactory.

The simulated SAR values and temperature distributions are compared with the

measured results reported in the paper, and my thermal analysis setup is verified.

Besides this antenna gives the idea to design an antenna which have large SAR values

in its neighborhood. One should design an antenna whose structure resembles the

already designed coaxial slot antenna.

After meetings with my principal investigator and some literature review, I

decided to use C type slotted antenna. After optimizing its performance and analyzing

mechanically I observe that the C-type antenna has a better performance in terms of

heating. But the temperature is still below 40 °C, which was the performance evaluation

criteria.

The heating strongly depends on the antenna type. More antenna types should

be reviewed and tested later in my project.

I would love to emphasize the fact that it is really hard to simulate an exact

medium and observe the heating in that medium. For instance, the C type antenna is

simulated inside human bone. But the real human bone consists of different parts and

materials. Its thermal and dielectric properties strongly depend on ambient conditions

and it is not homogenic as it is assumed in simulations. The software I used for heating simulations was Ansys Workbench, which is a software environment for performing

structural, thermal and electromagnetic analyses. It was a little bit hard for me learning

how to use this software for biomedical purposes, because the documentation on the

internet was restricted.

### 3.2 Future Work

In the following stages of my project, I would like to design an antenna that

shows more effective and better heating performance. I want to design and test a few

different antennas and specify the antenna I want to prototype until the beginning of

new semester. In EE 492, I will complete the simulations and start prototyping, and then

of course measurements.

### 3.3 Social, Environmental and Economic Impact

Although from an economical point of view, the project does not aim for any

profit or further labor, if the project will turn out to be a real success at the end of EE

492, then it will yield a great economic and social benefits for users and device

manufacturers. Moreover, using the designed antenna will save the patients and

physicians a lot of time, because the implant antenna has its own feedback mechanism.

Implicitly it will reduce the cost associated with the healthcare and it will improve the

healthcare provided. It is a fact that implanted wireless devices are going to find wider

application in tomorrow’s world. Whether my project will be completed successfully is

not going to change this fact.

### 3.4 Cost Analysis

The project required a workstation on which the simulations to be implemented. I

used the workstation of BOUNTENNA during my project. To create the measurement

setup a vector network analyzer (VNA), a rotary stage and absorbers will be used (in

EE 492). Moreover, I invested a specified amount of time for this project throughout

the year.

### 3.5 Standards

In this project, the engineering ethics and code of conduct is considered. Besides,

the IEEE, IET, ETSI and EU standards will be followed in addition to Turkish standards.

BIBLIOGRAPHY

BIBLIOGRAPHY

[1] OECD (2017), “Hip and knee replacement”, in Health at a Glance 2017: OECD Indicators, OECD Publishing, Paris.
[2] Third AJRR Annual Report on Hip and Knee Arthroplasty Data. (2016). [ebook] Rosemont, Illinois: American Joint Replacement Registry, pp.13-21. Available at: http://www.ajrr.net/images/annual_reports/AJRR_2016_Annual_Report_final.pdf [Accessed 21 Feb. 2019].
[3] Vanhegan, I. S., Malik, A. K., Jayakumar, P., Islam, S., Haddad, F. S. 2012. “A financial analysis of revision hip arthroplasty: the economic burden in relation to the national tariff”, J Bone Joint Surg Br, 94(5), 619-623.
[4] The NJR Editorial Board, Ed., “National Joint Registry 13th Annual Report 2016,” rep., 2016.
[5] L. Montanaro, P. Speziale, D. Campoccia, S. Ravaioli, I. Cangini, G. Pietrocola, S. Giannini, and C. R. Arciola, “Scenery of Staphylococcus implant infections in orthopedics,” Nov-2011. [Online]. Available: https://www.futuremedicine.com/doi/pdf/10.2217/fmb.11.117. [Accessed: 20-Feb-2019].
[6] G. D. Ehrlich, F. Z. Hu, Q. Lin, J. W. Costerton, and J. C. Post, “Intelligent implants to battle biofilms | Request PDF,” 03-Nov-2004. [Online]. Available:
https://www.researchgate.net/publication/292688877_Intelligent_implants_to_battle_biofilms. [Accessed: 20-Feb-2019].
[7] | S. Dumanli, “A cornered shallow cavity backed slot antenna suitable for smart hip implants,” | 2016 10th
| European Conference on Antennas and Propagation (EuCAP), 2016.
[8] H. Qi, K. Xiao, F. Zhao, S. Chai, and W. Yin, “A Design of Wide Band and Wide Beam Cavity-Backed Slot Antenna Array with Slant Polarization,” International Journal of Antennas and Propagation, 23-Oct-2016. [Online]. Available: https://www.hindawi.com/journals/ijap/2016/8980495/. [Accessed: 07-Mar-2019].
[9] Ilka Dove, “Analysis of Radio Propagation Inside the Human Body for in ...,” Aug-2014. [Online].
| Available: http://essay.utwente.nl/66071/1/Dove_MA_TE.pdf. [Accessed: 10-Mar-2019].
[10]Itis.swiss. (2019). DATABASE » IT'IS Foundation. [online] Available at: https://itis.swiss/virtual-
| population/tissue-properties/database/ [Accessed 11 Mar. 2019].

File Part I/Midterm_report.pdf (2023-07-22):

EE491

# Senior Design Project Midterm Report

# Design of an implantable antenna for microwave hyperthermia

## Submitted by: Aydın Uzun

## Principal Investigator: Sema Dumanlı Oktar

20.03.2019

### 1. Introduction

The recent technological advancements are revolutionizing the way healthcare is being delivered and they are also a key factor driving the advances of surgical treatment. Joint replacement surgery (hip and knee replacement) is considered the most effective intervention for severe osteoarthritis and hip fractures, reducing pain and disability and restoring some patients to near normal function. [1] As a consequence, hip replacement surgery shows increasing trends in most OECD countries. On average, the rate of hip replacement increased by 30% between 2000 and 2015.[1] Revision burden can be seen as a rough measure of the success of hip replacement surgeries. In the USA the revision burden was 10.2% for hips between 2012 and 2015 [2], but revision surgery of the hip is expensive owing to the increased cost of pre-operative investigations, surgical implants and instrumentation. [3]

The six most common indications for revision after primary hip replacement (listed in order of frequency) are aseptic loosening, pain, adverse soft tissue reaction to particulate debris, dislocation, infection and peri-prosthetic fracture.[4] Especially performing the revision surgery for infection is riskier considering the instrumentation. Staphylococcus aureus and Staphylococcus epidermidis are the leading etiologic agents of orthopedic implant infection.[5] Traditional antibiotic therapy will never be successful against these pathogens after the biofilm is formed. [6] This property of bacteria is called antimicrobial resistance (AMR) and it is a major concern worldwide. The other modes of treatment will be needed to prevent biofilm formation in the first place.

A hip implant can be equipped with sensors and microelectronics forming a wireless communication link between the implant and an on-body sensor to collect continuous data or provide real-time feedback.[7] In this project it is aimed to design an antenna taking action against infection before and during the biofilm formation through microwave hyperthermia with the help of the feedback from the antenna which monitors its environment.

### 2. Objectives

The objective of this project is to take action against infection through microwave hyperthermia. In this context, the electrical characteristics of the tissue surrounding the implant will be determined immediately after the operation. (when the infection is present) In addition to that, numerical and physical modelling of the propagation environment will be performed. After all of the optimizations are completed, the optimum working frequency for the microwave hyperthermia will be determined and the antenna design will be completed.

The second objective of this project is to develop the phantom and to build the measurement setup on which the measurements will be performed next semester.

### 3. Approach and Methodology

a. Optimizations for microwave hyperthermia

Because the human body absorbs electromagnetic waves it is often difficult to connect an implanted device to the outside world. The effect of hyperthermia depends on the depth of the implant, surrounding tissues and near field losses. It should be noted that the surrounding tissue properties and depth of the implant vary from patient to patient, but only in one patient as the patient ages. Therefore, an antenna which can adapt to the changing environment and target energy to the required region should be designed for microwave hyperthermia. The antenna parameters will be optimized considering both the thermal and electromagnetic distribution.
b. Phantom development and building of measurement setup

1- Digital 3D design of the phantom model

A 3D model will be developed to mimic the environment in which the hip implant will be located in real life. The model should include the hip implant, a portion of the femur, pelvis, body fluid, hip muscle, fat and skin.
2- The integration of 3D phantom model with liquid/gel phantoms

The printed 3D model should be filled up with liquid/gel in accordance with the approximate dielectric constant and conductivity values of the corresponding parts described above.
3- Development of measurement setup

A test kit will be developed for measuring the input response and the transmission response of the designed antenna. The test kit will consist of a mini vector network analyzer (VNA), a rotary stage and absorber material. The test kit will be used in system level tests too.

### 4. Work Completed

a. Literature review

After literature review it is decided to use a cavity-backed slot antenna, because the cavity backed slot antenna (CBSA), where the slot is backed with rectangular cavity, achieves unidirectional radiation and has advantages of low profile, light weight and ease of integration. [8] The CBSA can be fed by probe, metal waveguide, substrate integrated waveguide (SIW), and microstrip, but the microstrip-fed CBSA has simple structure and small size. [8]
b. Power density based and temperature-based optimization in single layer
a. Antenna design in vacuum

In this step a CBSA is designed to operate at 2.4 GHz. The industrial, scientific and medical (ISM) 2.40 GHz radio band is an allowed band for body area networks or medical applications. [9] The performance of designed antenna is judged by its return loss and radiation pattern.

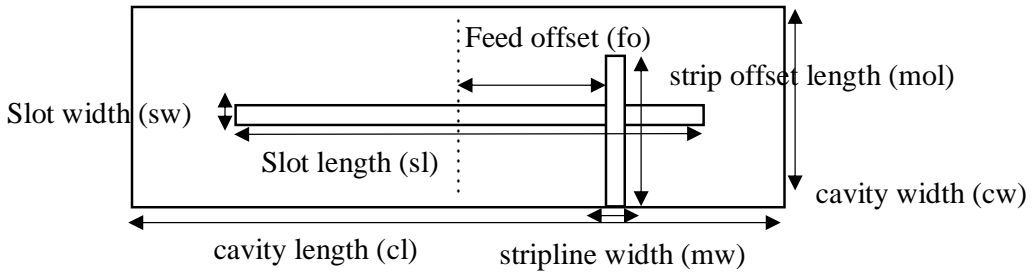
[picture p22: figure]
Slot length (sl); Slot width (sw); ……………… Feed offset (fo); cavity length (cl); cavity width (cw); stripline width (mw); strip offset length (mol)

The model of the designed antenna can be seen in Fig. 1, Fig. 2 and Fig. 3 from different perspectives. The dimensions of the model can be found in Table I.

The cavity is formed from a 3.15 mm thick (cavity height) substrate with a dielectric constant of 4.4 (FR-4). The slot is fed by a 50Ω stripline located in the vertical midplane of the antenna in z direction.

The initials dimensions other than the cavity height are determined using the HFSS Antenna Toolkit Software. Prior to the start of the optimization, the software introduces a microstrip feed slot antenna with the initial values of Table I, but this is not the desired antenna. After some modifications, the desired antenna is achieved, the model of which is shown in Fig. 1, Fig. 2. And Fig. 3.

The CBSA has been optimized for operation at 2.4 GHz with -20dB return loss. The optimization is done using software ANSYS Electromagnetics Suite. The dimensions given in Table I are parametrized and optimized for a return loss -20dB.

One conclusion that can be drawn from the optimization process is that the most critical parameters for matching are the parameters for the width of the stripline and the length of the stripline. In addition, sloth length is the most critical parameter in terms of CBSA resonance frequency.

z

y

cavity height (ch)

cavity length (cl)

Fig. 1. Modelled antenna in yz plane

Fig. 2. Modelled antenna in xy plane

y

x

x

z

…..

Feed offset (fo)

stripline width (mw)

Fig. 3. Modelled antenna in xz plane

cavity width (cw)

cavity height (ch)
stripline offset length (mol)

The return loss curve of the optimized antenna can be seen in Fig. 4.

Dimension | Initial value | Final value
Slot length | 5.56 cm | 5.2 cm
Slot width | 0.28 cm | 0.21 cm
Feed Offset | 1.55 cm | 1.8 cm
Stripline width | 0.31 cm | 0.15 cm
Stripline offset length | 1.71 cm | 0.53 cm
Cavity length | 11.1 cm | 8.1 cm
Cavity width | 8.3 cm | 3.2 cm

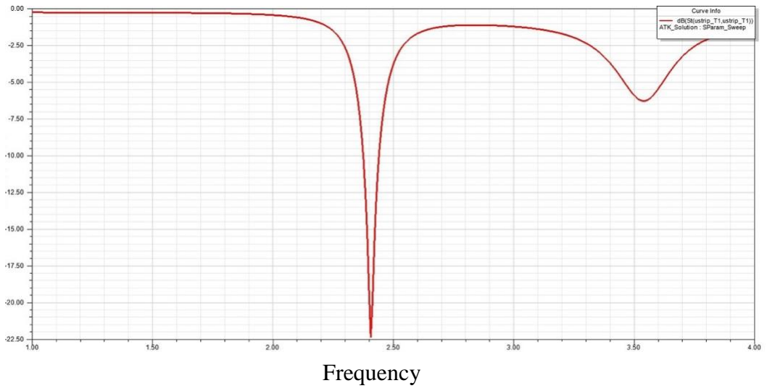
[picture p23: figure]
Frequency

b. Antenna design in fat

The same procedure is used as in vacuum. The initial values of parametrized dimensions of the antenna optimized in fat are the final values of the antenna optimized in vacuum. It is obvious that the dimensions should change significantly to cause a return loss of -20dB, since the electrical properties of vacuum and fat are completely different. The dimensions of the model shown in Fig. 1,2 and 3 are shown in Table II. The return loss curve of the optimized antenna can be seen in Fig. 5.

Dimension | Initial value | Final value
Slot length | 5.2 cm | 3.6 cm
Slot width | 0.21 cm | 0.06 cm

Table 1. Parametrized dimensions of CBSA in vacuum

Table II. Parametrized dimensions of CBSA in fat

Fig. 3. Simulated S11 vs Frequency

|S11| (dB)

Feed Offset | 1.8 cm | 0.1 cm
Stripline width | 0.15 cm | 0.22 cm
Stripline offset length | 0.53 cm | 1.1 cm
Cavity length | 8.1 cm | 4.8 cm
Cavity width | 3.2 cm | 2.5 cm

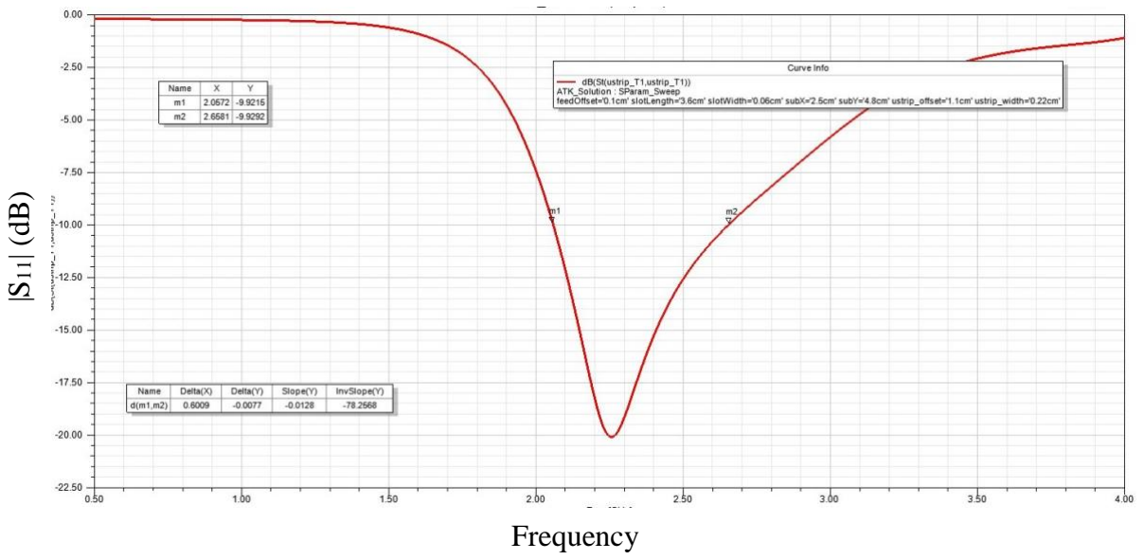
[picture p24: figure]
Frequency

c. Transient thermal analysis of designed antenna
a. Single layer

The model is already set up in HFSS to prepare it for thermal analysis. The HFSS geometry and the associated solution data should be transferred to ANSYS Workbench and the thermal analysis carried out in ANSYS Workbench. The thermal properties of the materials should be introduced to the software. [10] Thereafter, heat dissipation should be specified by assigning convection to the exterior surfaces of the structure. In addition, it should be introduced into software which objects introduce heat effect to calculate the thermal properties. There are two types of imported loads: heat flux, heat generation. The designed model should have both, because there exist volume losses caused by currents flowing in the volumes of lossy dielectrics and surface losses caused by currents flowing in the volumes of lossy dielectrics. After completing these steps, the temperature of the entire model can be displayed.

The first demo I achieved is shown in Fig. 5. Although it looks quite good and appears to satisfy the aforementioned evaluation criteria, namely whether the 1mm neighborhood of the designed antenna can be heated to 40°C, the demo in Fig. 5 does not reflect the truth. Because I have found that the system power for gain calculations is not 0.1W as intended. I believe that I can fix this problem soon.

Fig. 4. Simulated S11 vs Frequency

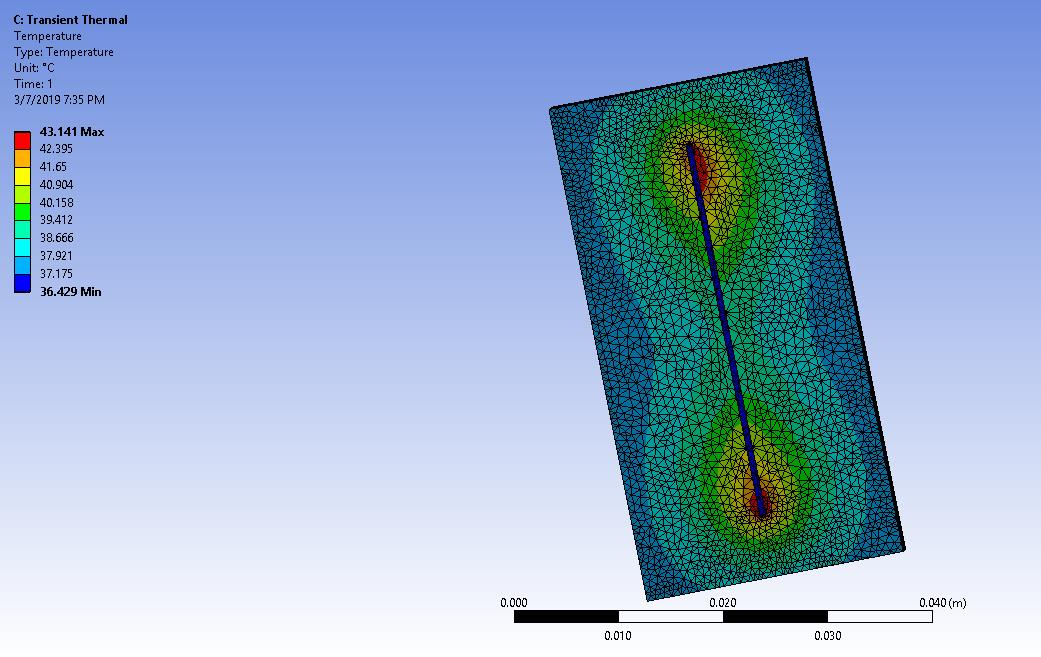
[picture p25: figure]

### 5. Work to Be Completed

Power-density-based
optimization

Cylindrical Layer

20.03.2019 – 19.04.2019

Detailed Layer

Temperature-based
optimization

Cylindrical Layer

Detailed Layer

Phantom development and building of measurement setup | 19.04.2019 – 13.05.2019
Report & Presentation | 13.05.2019 – 27.05.2019
Prototyping | Antenna element | EE 492

Phantom

Measurements | System level measurements
| Heating measurements

Report & Presentation

The antenna parameters will be optimized using outputs of each layer structure as feedbacks step by step from the simplest one (single layer) to the most complicated one (detailed layer) considering both power density-based optimization and temperature-based optimization and hence, they will be considered as a whole.

### 6. Realistic Constraints

a. Social, Environmental and Economic Impact

Fig. 5. Transient Thermal Analysis

Although from an economical point of view, the project does not aim for any profit or further labor, if the project will turn out to be a real success, then it will yield a great economic and social benefits for users and device manufacturers. Moreover, using the designed antenna will save the patients and physicians a lot of time, because the implant antenna has its own feedback mechanism. Implicitly it will reduce the cost associated with the healthcare and it will improve the healthcare provided. It is a fact that implanted wireless devices are going to find wider application in tomorrow’s world. Whether my project will be completed successfully is not going to change this fact.
b. Cost Analysis

The project requires a workstation on which the simulations to be implemented. I will be using the workstation of BOUNTENNA during my project. To create the measurement setup a vector network analyzer (VNA), a rotary stage and absorbers will be used. In addition to these costs, a 3D printer and chemicals will be used to create the phantom which should imitate the biological tissue. These materials should also be included in the costs. Moreover, I will be investing a specified amount of time for this project throughout the year. My plan is to work at least for three days each week for a faster progress.

c. Standards

In this project, the engineering ethics and code of conduct will be considered. Besides, the IEEE, IET, ETSI and EU standards will be followed in addition to Turkish standards.

### 7. References

[1] OECD (2017), “Hip and knee replacement”, in Health at a Glance 2017: OECD Indicators, OECD Publishing, Paris.
[2] Third AJRR Annual Report on Hip and Knee Arthroplasty Data. (2016). [ebook] Rosemont, Illinois: American Joint Replacement Registry, pp.13-21. Available at: http://www.ajrr.net/images/annual_reports/AJRR_2016_Annual_Report_final.pdf [Accessed 21 Feb. 2019].
[3] Vanhegan, I. S., Malik, A. K., Jayakumar, P., Islam, S., Haddad, F. S. 2012. “A financial analysis of revision hip arthroplasty: the economic burden in relation to the national tariff”, J Bone Joint Surg Br, 94(5), 619-623.
[4] The NJR Editorial Board, Ed., “National Joint Registry 13th Annual Report 2016,” rep., 2016.
[5] L. Montanaro, P. Speziale, D. Campoccia, S. Ravaioli, I. Cangini, G. Pietrocola, S. Giannini, and C. R. Arciola, “Scenery of Staphylococcus implant infections in orthopedics,” Nov-2011. [Online]. Available: https://www.futuremedicine.com/doi/pdf/10.2217/fmb.11.117. [Accessed: 20-Feb-2019].
[6] G. D. Ehrlich, F. Z. Hu, Q. Lin, J. W. Costerton, and J. C. Post, “Intelligent implants to battle biofilms | Request PDF,” 03-Nov-2004. [Online]. Available:
https://www.researchgate.net/publication/292688877_Intelligent_implants_to_battle_biofilms. [Accessed: 20-Feb-2019].
[7] | S. Dumanli, “A cornered shallow cavity backed slot antenna suitable for smart hip implants,” | 2016
| 10th European Conference on Antennas and Propagation (EuCAP), 2016.
[8] H. Qi, K. Xiao, F. Zhao, S. Chai, and W. Yin, “A Design of Wide Band and Wide Beam Cavity-
| Backed Slot Antenna Array with Slant Polarization,” International Journal of Antennas and
| Propagation, 23-Oct-2016. [Online]. Available:
| https://www.hindawi.com/journals/ijap/2016/8980495/. [Accessed: 07-Mar-2019].
[9] Ilka Dove, “Analysis of Radio Propagation Inside the Human Body for in ...,” Aug-2014. [Online].
| Available: http://essay.utwente.nl/66071/1/Dove_MA_TE.pdf. [Accessed: 10-Mar-2019].
[10]Itis.swiss. (2019). DATABASE » IT'IS Foundation. [online] Available at: https://itis.swiss/virtual-
| population/tissue-properties/database/ [Accessed 11 Mar. 2019].

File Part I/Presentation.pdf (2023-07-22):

## DESIGN OF AN IMPLANTABLE ANTENNA FOR MICROWAVE HYPERTHERMIA

PI : Sema Dumanlı OKTAR
Evaluation Committee Members : Arda Deniz YALÇINKAYA
İlke ERCAN

# INTRODUCTION

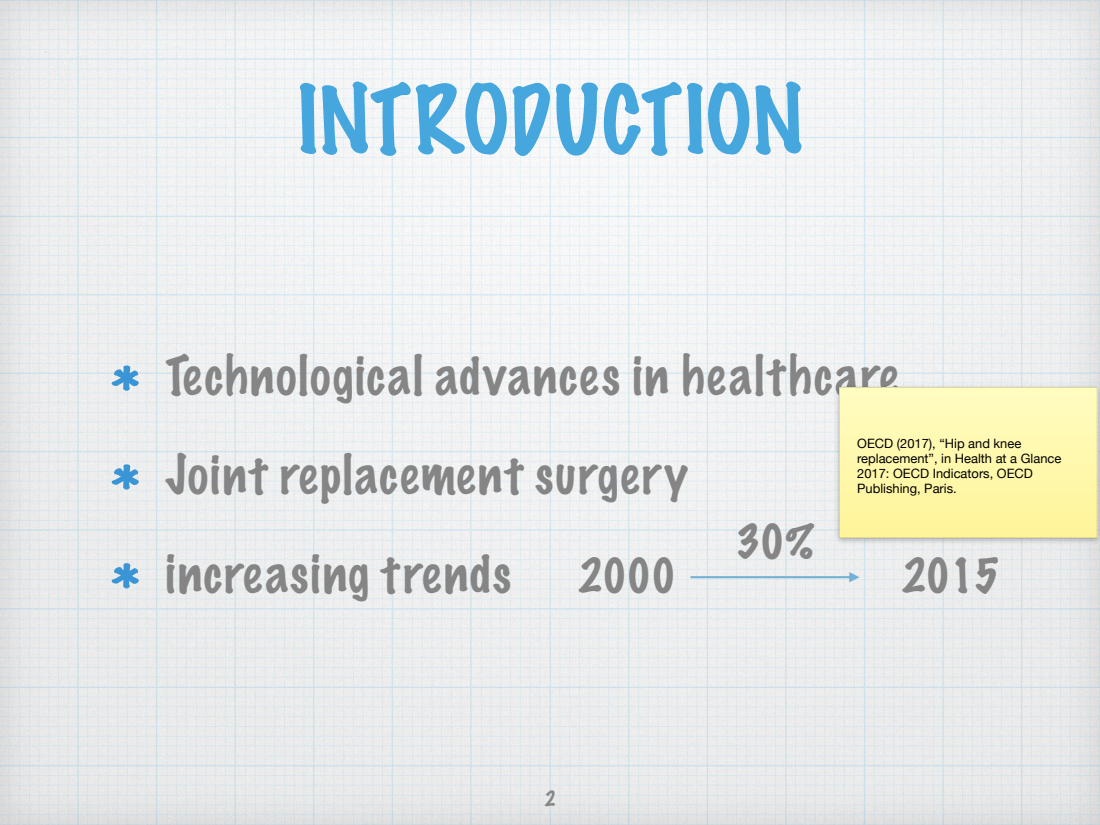
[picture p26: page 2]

Technological advances in healthcare
Joint replacement surgery
increasing trends

OECD (2017), “Hip and knee
replacement”, in Health at a Glance
2017: OECD Indicators, OECD
Publishing, Paris.

# INTRODUCTION

Revision surgery | expensive , risky
Why revision surgery ? | Infection

3

# INTRODUCTION

Antibiotic therapy; not successful; Why ?; AMR

The agents of implant infection :
Staphylococcus aureus, Staphylococcus
epidermidis
An antenna taking action against infection
before and during biofilm formation

# CBSA

Microstrip-fed CBSA; simple structure

Why CBSA?
In vacuum
2.4 GHz - ISM band

# The model


# Dimensions of the model

Conclusion : slot length; resonance; Matching; the width and the

optimisation process for operation at 2.4
GHz with -20 dB
frequency
length of the stripline


in vacuum

in fat

# Thermal analysis

ANSYS Workbench

Not satisfactory : from 37 °C to 37. 13 °C

Antennas for telecommunication : radiation pattern

Antennas for thermal treatment : SAR

# SAR Field of CBSA


# Coaxial Slot Antenna


Measured SAR distribution

Simulated SAR distribution

# Thermal analysis Setup

Net input power : 5 W

Heating time : 600s

İnitial temperature (muscle): 37 ºC.


Simulated
temperature
distribution

Measured temperature
distribution

## Antenna with C-type slots


Simulated SAR distribution of the designed antenna

# Thermal Analysis

Temperature : 37 °C 38.53 °C

Does not meet the performance evaluation criterion

# Future Work

Design an antenna that shows better heating performance

Specify the antenna that I want to prototype until the beginning of Fall 2019

In EE 492 complete simulations, start prototyping and measurements

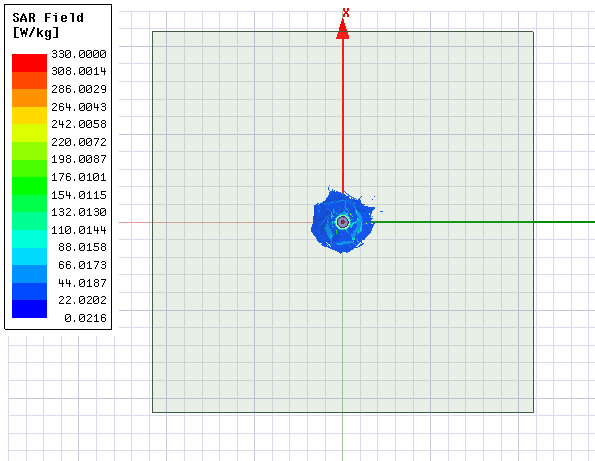
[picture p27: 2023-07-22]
Part I/figs/kochi_in_femur_sar_xy.PNG

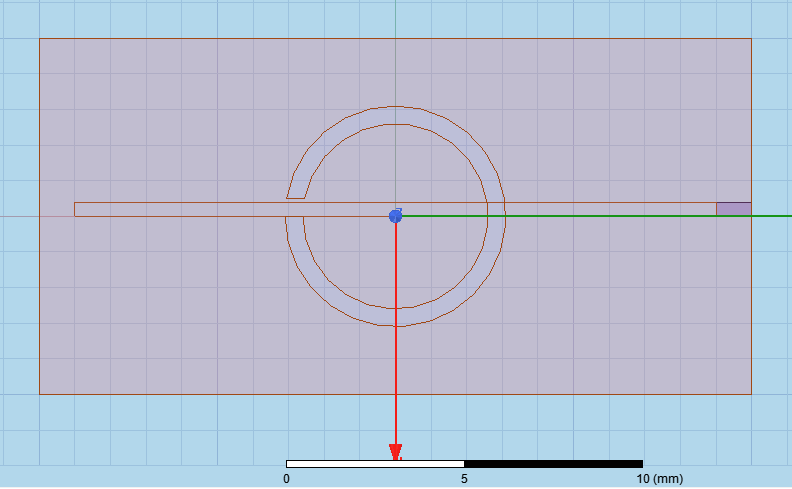
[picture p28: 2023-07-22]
Part II/figs/for2.5ghz.PNG

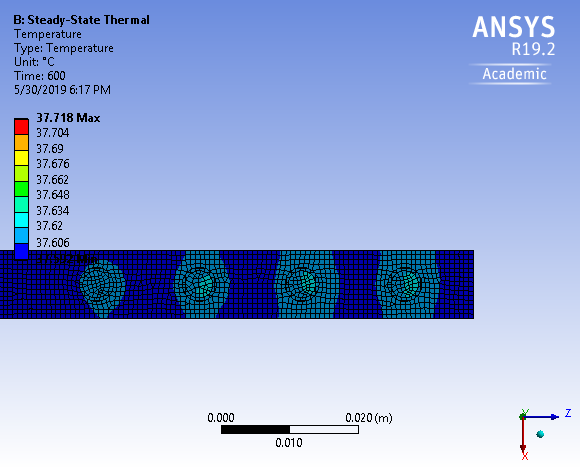
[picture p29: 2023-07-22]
Part I/figs/thermal_proposed.png

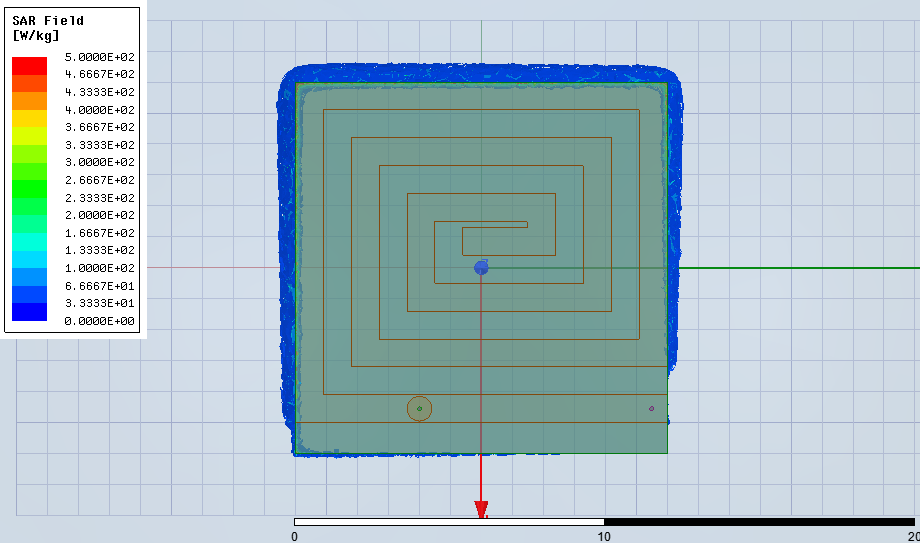
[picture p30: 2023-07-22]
Part II/figs/png3.PNG
